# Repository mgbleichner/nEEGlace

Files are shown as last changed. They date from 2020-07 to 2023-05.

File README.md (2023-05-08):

<div>
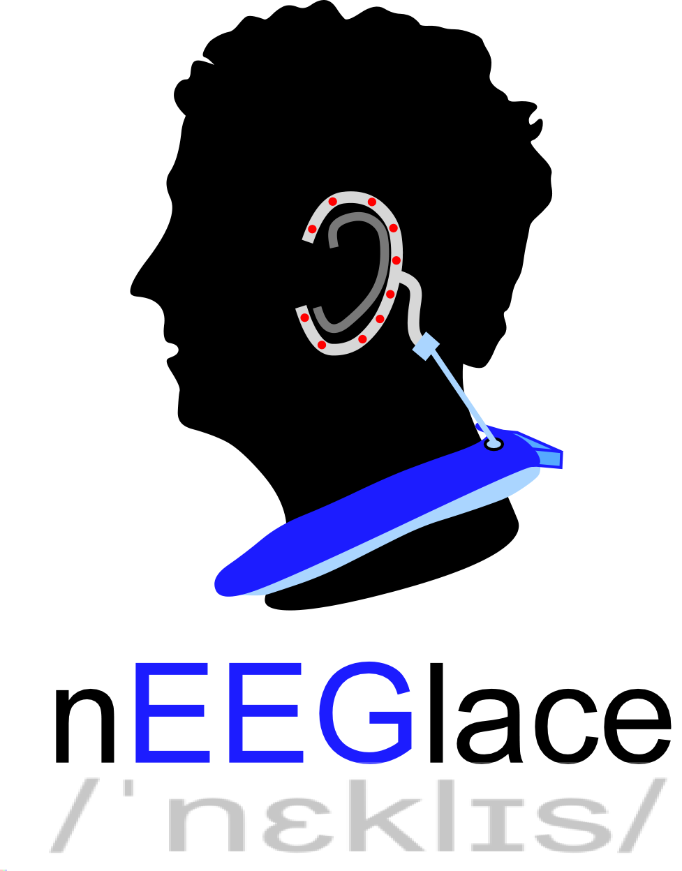
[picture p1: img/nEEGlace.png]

</div>

## nEEGlace
This is the project repository for the: **nEEGlace - a mounting system for EEG hardware for mobile ear-EEG recordings**

The nEEGlace is a system to record brain activity from electrodes located around the ears (cEEGrids). You can learn more about the cEEGrids [here](https://uol.de/psychologie/abteilungen/ceegrid), and instruction on how to use the cEEGrids can be found [here](https://www.jove.com/de/v/64897/recording-brain-activity-with-ear-electroencephalography) or [here](https://uol.de/en/psychology/neurophysiology/resources/ceegrid-video-tutorial). The nEEGlace is a combination of a commercial, research-grade EEG amplifier and a commercial neck speaker.  The system allows to conveniently record EEG over extended periods, and to play back sounds (e.g. for conducting studies in the field of auditory neuroscience).

The associated Hardware Metapaper in the Journal of Open Hardware can be found here: [Building an Ear-EEG System by Hacking a Commercial Neck Speaker and a Commercial EEG Amplifier to Record Brain Activity Beyond the Lab](https://openhardware.metajnl.com/article/10.5334/joh.25/)

Hardware:   

| nEEGlace |
|--------|
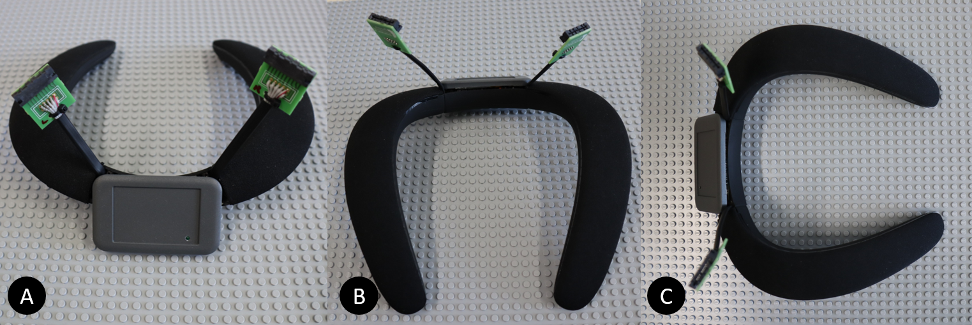
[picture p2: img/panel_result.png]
nEEGlace
|*The nEEGlace for beyond the lab ear-EEG recordings*|

## Before you Start
Before you start, read carefully through the entire document.  Be aware that you will lose all manufacturer warranty if you modify the devices as described below. 

As also stated in the [SMARTING User Manual](https://mbraintrain.com/wp-content/uploads/2016/08/SMARTING-User-Manual.pdf): Do not use the amplifier (i.e., the nEEGlace) while charging! 

## Components
* Neckspeaker - JBL Soundgear BTA [https://www.jbl.com/bluetooth-speakers/JBL+SOUNDGEAR+BTA.html](https://www.jbl.com/bluetooth-speakers/JBL+SOUNDGEAR+BTA.html)
* Smarting EEG Amplifier [https://mbraintrain.com/smarting/](https://mbraintrain.com/smarting/)
* cEEGrid Connectors [https://uol.de/neuropsychologie/howtoconnect](https://uol.de/neuropsychologie/howtoconnect)
* Female Jack Plug Socket

The cEEGrid is intended to be used with cEEGrids, the are available for example [here](https://shop.tmsi.com/product/).

## The Neck Speaker
The neck speaker serves primarily as a comfortable to wear mount for the 
amplifier and the connectors. In addition to that, it allows to play and record sound. 
The original Bluetooth functionality and any control functionality of the neck speaker is lost, as all active electronic components are removed from the neck speaker. The amplifier is positioned where the battery of the neck speaker was. 

## Disassemble Neck Speaker 
*  Remove mesh (A): The mesh material is clicked on the plastic part. The mesh material can be removed using a thin blade to lift it from the body. 
*  Unbolt all screws (B).
*  Remove the  metal plate in the middle (C).
*  Carefully lift the left part of the body (D). There is black glue at several locations,  remove carefully. 
*  Carefully lift the right part (E). The only thing that keeps the top part and body together is the micro USB connector.
*  Unbolt the screw (F).
*  Top (G-H) and bottom (I) parts are now detached from each other.

| Disassembly of Neck Speaker |
|--------|
|Disassembly Disassembly of neck speaker*Disassembly of neck speaker (A-I)*|

### Cut the Mesh

* Cut the mesh at the flexible joints (A - B).
* The center part is not needed and is left open for the amplifier (C).

| Mesh preparation |
|--------|
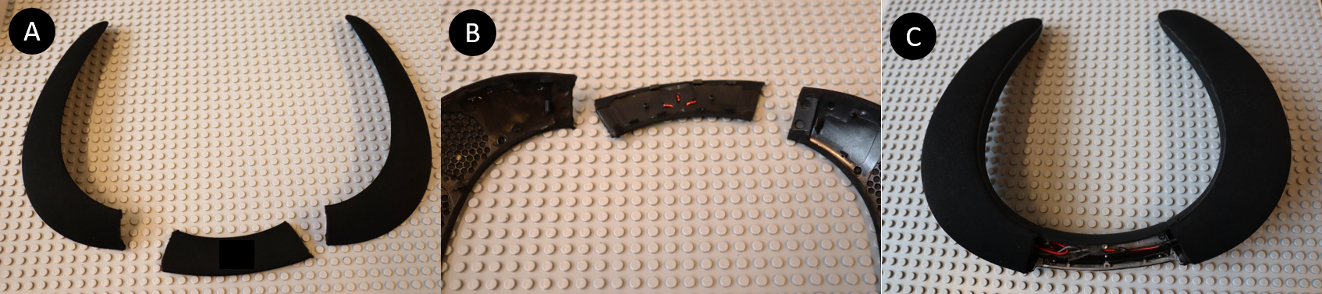
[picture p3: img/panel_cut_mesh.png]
Mesh preparation
|*Mesh preparation (A-C)*|

## Disassemble Amplifier 
* Remove the four grey plastic covers at the backside of the amplifier. 
* Unbolt the four screws at the backside of the amplifier. 
* Lift the backside from the amplifier. You find the amplifier board, the lithium battery and the connector (A). 
* Lift the amplifier out of the plastic casing (B).

`!!Do this at your own risk! If you do this, you will lose all manufacturer warranty! This may destroy your amplifier! The authors of this article are not responsible for any potential damage!`

* Before you unsolder the battery and the connector cable make sure that you know your channel layout.
* Unsolder the battery and the connector cable (C).

| Disassembly of Amplifier |
|--------|
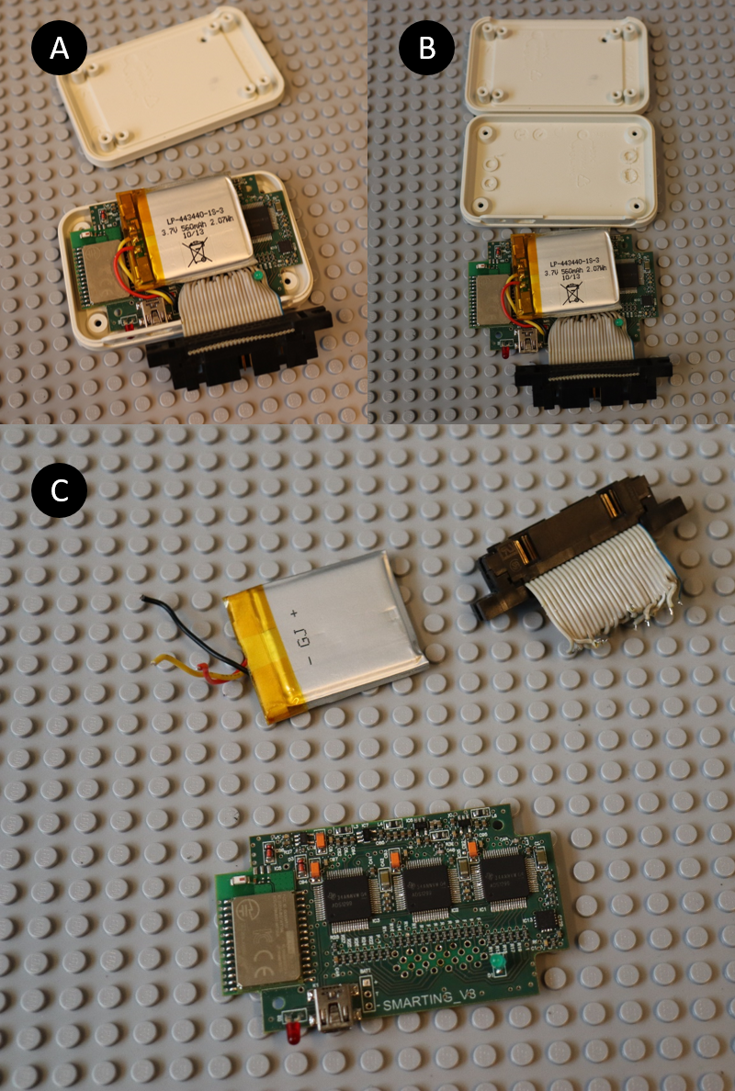
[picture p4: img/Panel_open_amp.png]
Disassembly of amplifier
|*Disassembly of amplifier (A-C)*|

## Making Room for Amplifier Casing
The amplifier will be placed in the center of the neck speaker (I, silver), where the batteries were located.
To make room for the amplifier casing, part of the neck speaker casing needs to be removed.
For this, we used a rotary power tool (Dremel). 

* Push the board as far as possible to the front edge of the neck piece (A, red arrow).
* Mark the left and right side. Add .5 cm on each side for the casing. 
* Mark the area you want to cut out (B-D).

| Prepare Casing |
|--------|
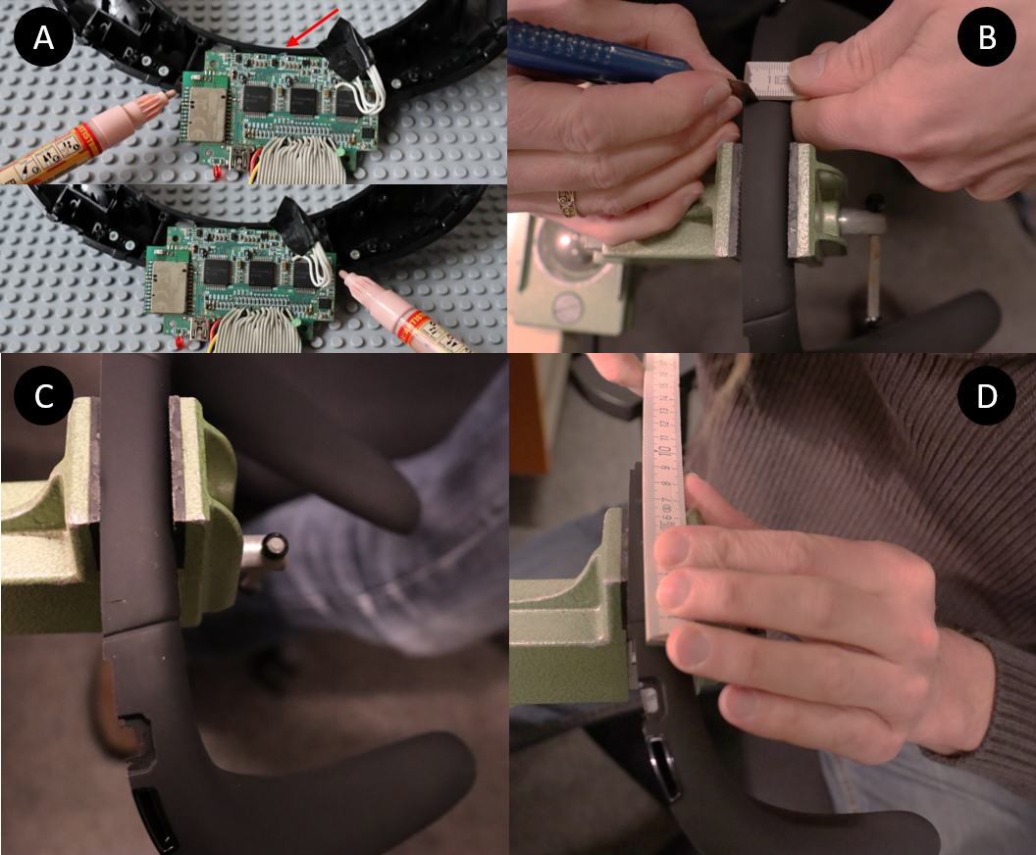
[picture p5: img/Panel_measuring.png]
Preparing casing
|*Preparing casing. Make room for the amplifier, A) The amplifier board needs to fit. Push the board as far as possible to the front edge of the neck piece (red) arrow. Mark the left and right side. Add .5 cm on each side for the casing. B-D) Mark the area you want to cut out.*|

| Cut casing |
|--------|
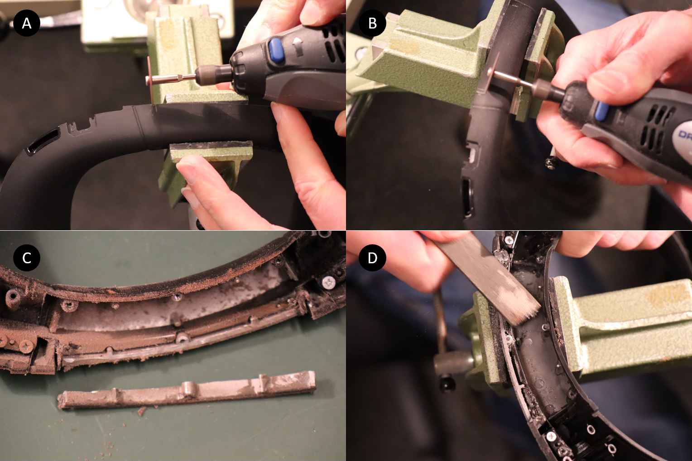
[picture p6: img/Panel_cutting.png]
Cut casing
|*Make vertical (A) and horizontal (B) cuts into the aluminum. Make sure to remove all cutting residuals (C) and clean the cutting edge (D).*|

* Make vertical (A) and horizontal (B) cuts into the aluminum. Make sure that you do not cut into the metal clasp (C).
* Remove all metal and rubber shavings (C).
* Clean the cutting edge (D) and remove again all metal shavings.
* The result is shown in figure X (A). 

## Adjust Amplifier Casing
The lower part of the amplifier will be glued to the 
neck speaker and needs to be adapted to follow the curvature of the neck speaker.
This part of the amplifier casing and the neck speaker should be large enough to fit the amplifier board. 
* Mark the curvature of the neck speaker on the amplifier casing (B-C).
* Cut the amplifier with rotary power tool (D).
* The part of the casing marked here with an white X (E) can be discarded.
* There are a couple of plastic parts, inside the amplifier casing that need to be removed (F).

| Adjust  Amplifier Casing|
|--------|
|Adjust amplifier casing*Adjust the amplifier casing*|

## Combine Amplifier Casing and Neck Speaker Casing
The amplifier casing is glued onto the neck speaker. 
* Remove all residual rubber  (A) to expose the bare metal (B).
* Put the neck piece a bit higher (C).
* Place the amplifier casing at the corresponding location.
* Place something behind the casing to keep it in place.
* Glue the casing with 2-components Epoxy glue https://www.uhu.com/en/product-page.5485
* Let dry for at least 12 hours. 
* Turn the neck piece over and add another stripe of glue on the backside. 

| Add Casing|
|--------|
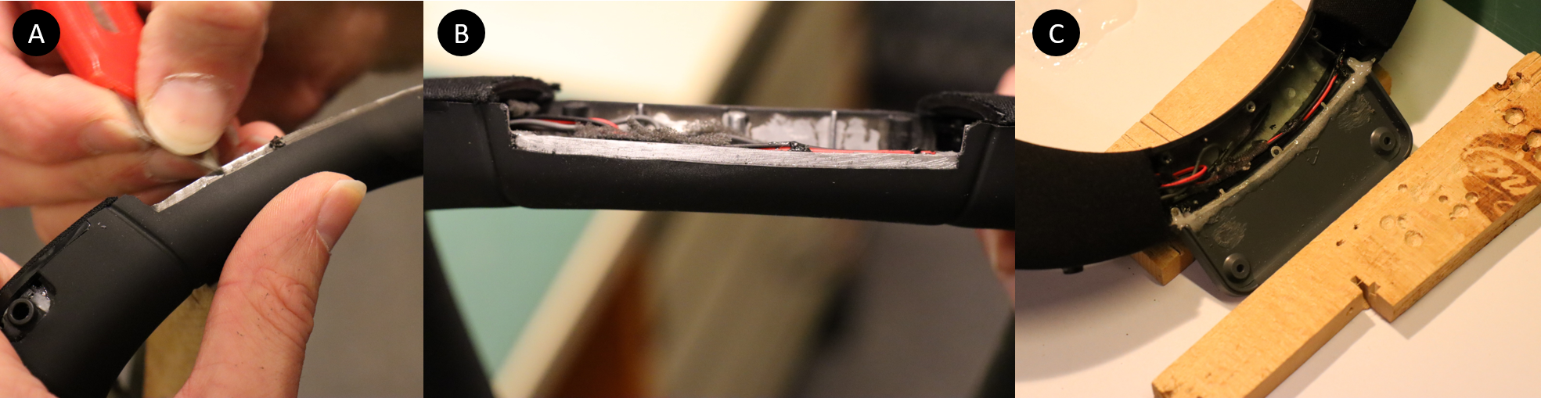
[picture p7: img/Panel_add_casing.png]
Add casing
|*Add casing*|

## Adding the Jack Plug Socket
The neck speaker comes with Bluetooth. As the smarting amplifier communicates 
with Bluetooth as well, and as two Bluetooth connecting to a single devices are 
not possible, the neck speakers Bluetooth capabilities are removed.  
Furthermore, we had to remove the battery of the neck speaker to make room for 
the amplifier. To still be able to use the speaker and microphone functionality 
we added a jack plug socket.

### Making Room for the Jack Plug Socket
The jack plug socket goes where the neck speakers micro USB connector was. 
The area is large enough for a jack plug socket if you make the hole a bit larger (see pictures). 

* Remove the part of the plastic as indicated on (A) with pliers (B).
* The resulting hole (C) is just large enough to put the jack plug socket in (D), for a snug fit.

| Making Room for Jack Plug Socket|
|--------|
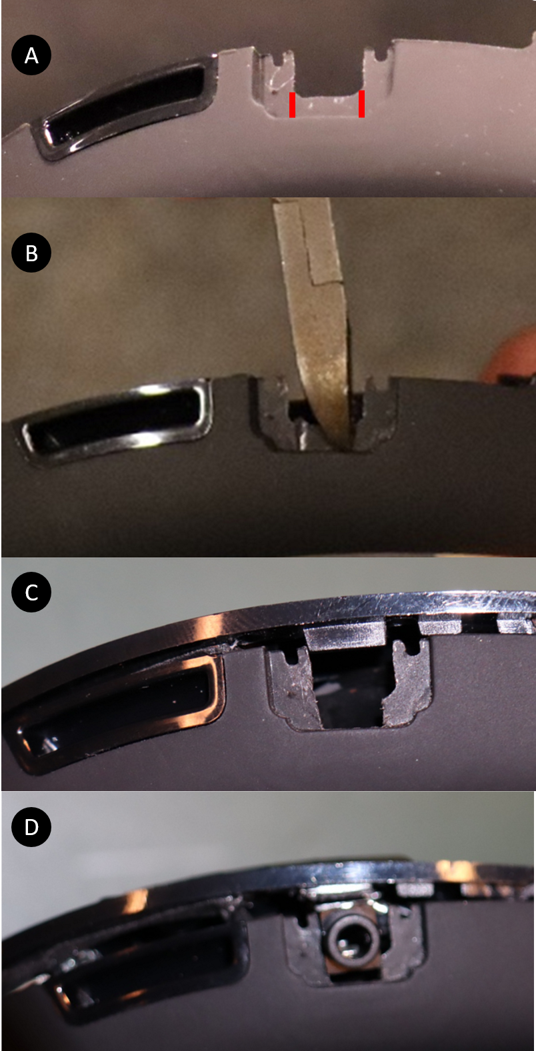
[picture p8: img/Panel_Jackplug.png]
Making room for jack plug socket
|*Making room for jackplug*|

### Remove Original Wiring of Neck Speaker
* Remove all glue and foamed material (A - B).
* Remove control unit (C).
* Remove microphone (grey cable) on the right side (D).
* Cut speaker cable on the right side (E - F).
* Remove everything but the speakers and the respective cabling from the neck piece (G).
* View from below (H) and from above (I). Left and right side are not connected. 
* We end up with a red/black cable for the speakers and a grey cable for the microphone. 

| Remove Wiring|
|--------|
|Remove wiring*Remove wiring*|

### Connecting the Jack Plug Socket
* Prepare the speaker cable to connect to the jack plug socket and solder them like in the following picture:

### Prepare cEEGrid connectors
The cEEGrid connector has been designed to fit into mini edge card sockets as 
offered by [SAMTEC (MB1-120-01-L-S-01-SL-N)](https://www.samtec.com/products/mb1). 
In combination with a small proprietary printed circuit board (PCB, shown below), 
a flat-ribbon cable and touch-proof (or similar) connectors, cEEGrids can be 
connected to most available EEG systems. To facilitate soldering and lower the 
risk of bridges we recommend removing every second pin before assembling the connector. 
Beginning with Pin 1, you have to remove every 2nd pin from the connector (see below).

If you want to produce or modify our connector, visit the fritzing website. 
[Download this file](https://uol.de/f/6/dept/psycho/cEEGrid/pdf/smarting_mit_logo.fzz) for printing the PCB there. Alternatively, you can find the PCB desings [here](./cEEGrid-Adapter) as Gerber file. 

| Prepare Connectors|
|--------|
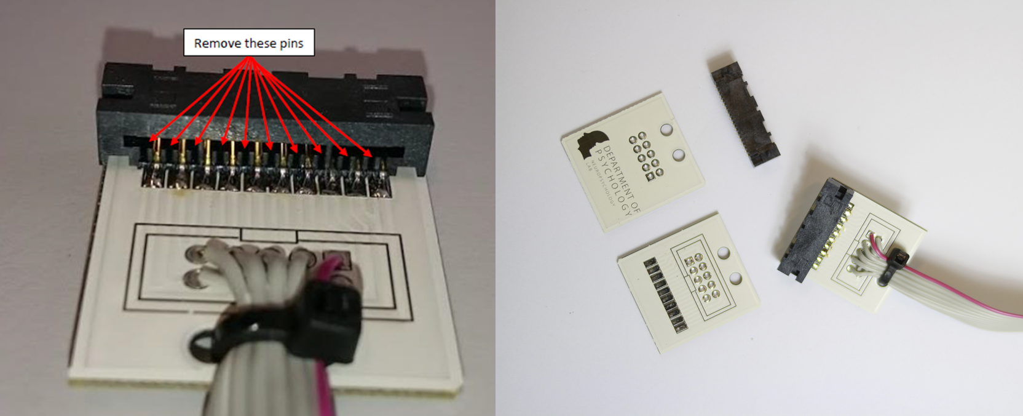
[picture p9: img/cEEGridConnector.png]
Prepare connectors Prepare Connectors
|*Left: to lower the risk of bridges between channels, we recommend removing every second pin before assembling the conector. Right: The PCB and mini card sockets before and after assembly.*|

| Soldering Instruction|
|--------|
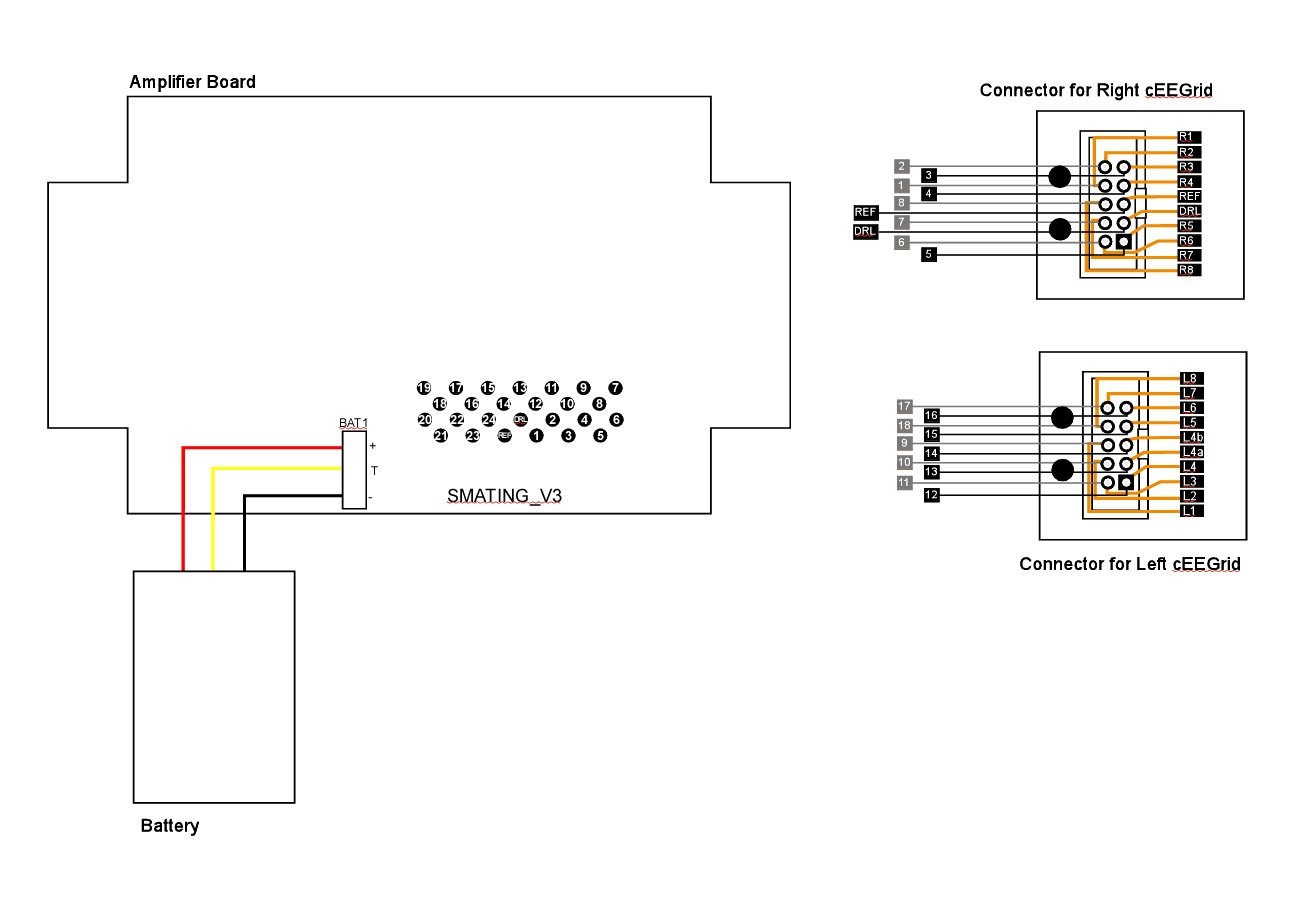
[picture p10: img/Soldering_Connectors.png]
Soldering Instruction Soldering Instruction
|*Schematic of channel configuration of amplifier board and cEEGrid connectors. Mark that the connectors for the left cEEGrid and right cEEGrid connector are inverted. The schematic for connecting amplifier and connectors can be found [here](./img/Soldering_Connectors.pdf)*|

* In our setup, channels R04a and R04b (i.e. right cEEGrid) serve as REF and DRL electrodes, respectively (in general you are free to choose the location of REF and DRL)

### Solder Connectors onto Amplifier. 
The connector cables can be soldered onto either the front or the back of PCB board of the amplifier. 
When you buy the smarting amplifier, the connector cables are on top. We place the cables from below. 
This allows us to position the cables in the neck piece. The pin arrangement of the amplifier can also be found in the [SMARTING User Manual](https://mbraintrain.com/wp-content/uploads/2016/08/SMARTING-User-Manual.pdf). 

* The connector cable should be about 5 cm long (A).
* The cables are connected on the backside (B, bottom). 
* The battery will remain on the front (B, top).
* Place the newly connected amplifier into the casing (C).
* Place the amp cover (D), and screw it on with the original screws (D).
* Cover the PCB board of the connector with shrink tubing to insulate the board

| Add Connectors|
|--------|
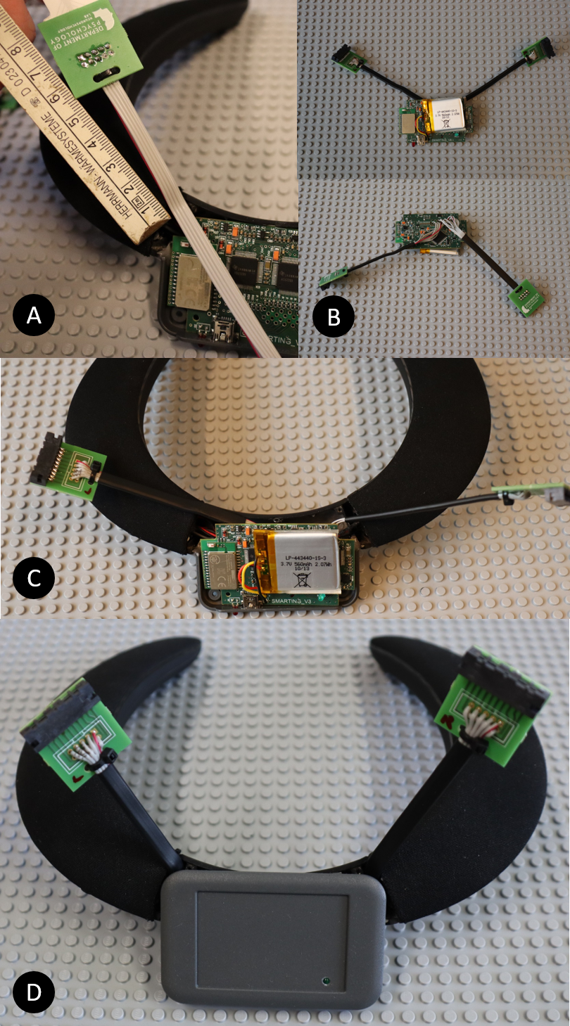
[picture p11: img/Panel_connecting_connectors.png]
Add connectors
|*Added cEEGrid connectors*|

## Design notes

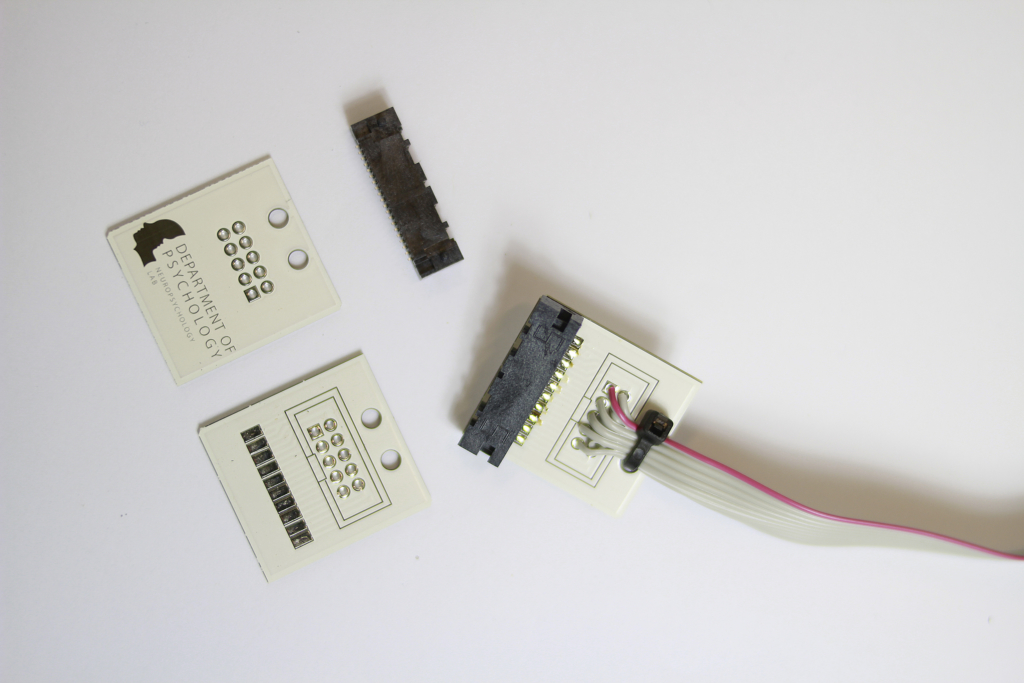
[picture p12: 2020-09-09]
img/cEEGridConnector.jpg

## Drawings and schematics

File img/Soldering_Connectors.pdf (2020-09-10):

## Connector for Right cEEGrid

## Amplifier Board

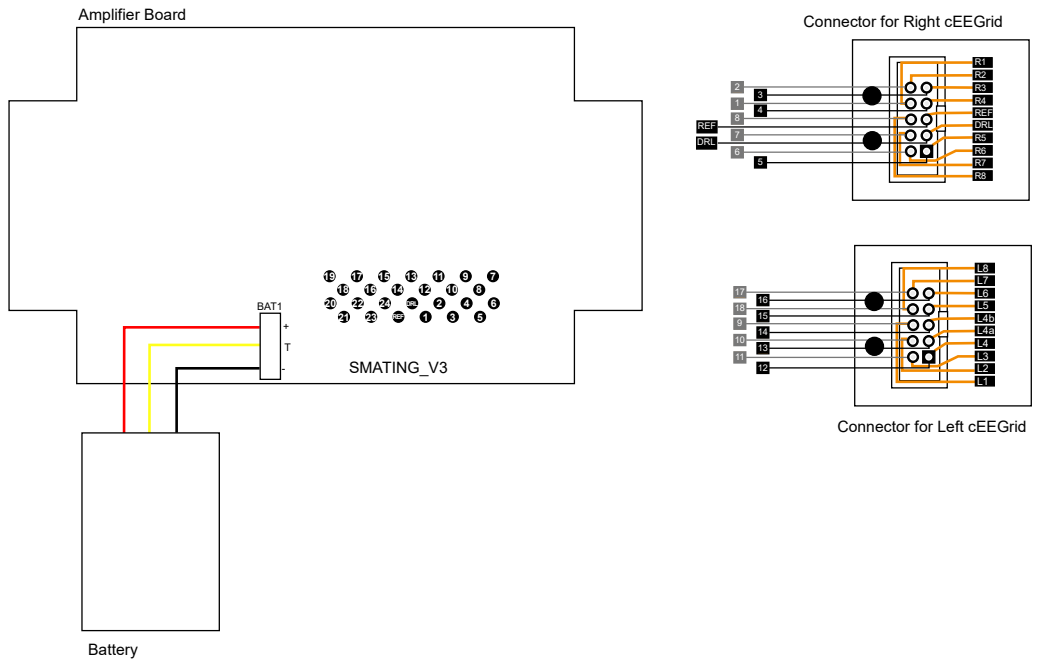
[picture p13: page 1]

Connector for Left cEEGrid

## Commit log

2020-08-31 Add PCB design as Gerber file, some minor text edits
    [smarting mit logo_contour.gm1, smarting mit logo_copperBottom.gbl, smarting mit logo_copperTop.gtl, smarting mit logo_maskBottom.gbs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]
2020-09-09 adding connector information
2020-09-10 Added instruction for soldering the connectors
2020-09-10 Soldering_Connectors.pdf added
2020-09-10 Soldering_Connectors.png added
2020-09-16 Update README.md
    Added shrink tubing statement

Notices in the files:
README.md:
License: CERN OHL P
